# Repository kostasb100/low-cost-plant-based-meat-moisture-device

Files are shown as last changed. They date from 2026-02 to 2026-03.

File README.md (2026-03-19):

# Low-Cost Plant-Based Meat Moisture Content Measurement Device Based on Raspberry Pi 4 B, Its Camera Module 3 NoIR, and a Halogen Lamp

This repository contains work conducted at the Optics and Photonics Laboratory at Niigata University by fourth-year Electronics, Information and Communication Engineering Program student Kostas Martynas Balciunas between 2025 and 2026 for his Bachelor's thesis. The purpose of this repository is to enable students and other individuals to recreate, use and potentially improve the moisture content measurement device that was developed during this period.

## The repository includes:
- Mechanical diagrams of the developed device  
- Software and programs used for the device and its measurement data analysis  
- Electrical circuit diagrams of the developed device  
- Additional materials to assist in recreating the device and the plant-based meat used

## Guide to those seeking to recreate the device:

1) Carefully read the Aim, Basic Theory, Current Results, and Future Work sections of this README.md file to understand the basic concepts of the developed measurement device and it's limitations.
2) Buy the necessary materials to build the measurement device (print the 3D model of the device and assemble the electrical circuits) and prepare the plant-based meat sample (other recipes for plant-based meat samples can also be used).
3) Set up your Raspberry Pi 4 B module (it may be possible to use other Raspberry Pi microcontrollers as well) and install the necessary libraries and software (refer to Programs).
4) Recreate the electrical circuits used in the measurement device (refer to Electrical Circuit Diagrams). Make sure they work as standalone circuits before connecting them to the microcontroller.
5) 3D print and construct the case for the measurement device (refer to Mechanical Diagrams). 3D printing the device is not necessary, since 2D diagrams are provided (Mechanical Diagrams/2D diagrams), and it is possible to recreate the device using cheaper materials such as cardboard or plywood. However, it is important to note that the precision of the measurement device may suffer due to the unevenness of individual components made by hand.
6) Install the electrical circuits and the Raspberry Pi Camera Module 3 NoIR into the case of the device.
7) Prepare the plant-based meat sample for the experiments (refer to Recipe of the plant-based meat used).
8) Conduct experiments and initial image processing using the user manual provided in the User Manual and Guide section of this repository.
9) Conduct comprehensive (batch) post-experiment image processing using Programs/Other Programs/apv_calculator.py.
10) Use other programs to visualize experiment results if necessary.
11) Learn, improve, and enjoy the process. If you notice any issues, make improvements or like to request for the actual data of the individual experiments conducted please contact the creator of this repository (contacts are listed at the bottom of this file).

## Aim
Interest in alternative proteins such as plant-based meats has grown in recent years, but development remains concentrated in regions like North America and Europe due to the need for expensive facilities and equipment. This limits access for developing countries and institutions with restricted budgets, potentially hindering global progress in this field.

Moisture content is a key parameter affecting the texture, taste, and overall quality of plant-based meat products and is typically measured using costly equipment such as spectrometers. This project investigates the feasibility of a low-cost, Raspberry Pi-based imaging device for non-destructive, real-time moisture measurement during product development. It also explores the use of the same device to track changes in moisture content, size, and color over time, providing insight into the sample’s optical and physical properties.

## Basic Theory

Water molecules are known to absorb electromagnetic radiation (light) over a wide range of the electromagnetic spectrum [1]. The relationship between wavelength and the corresponding absorption coeffcient is shown in Figure 1.

<p align="center">
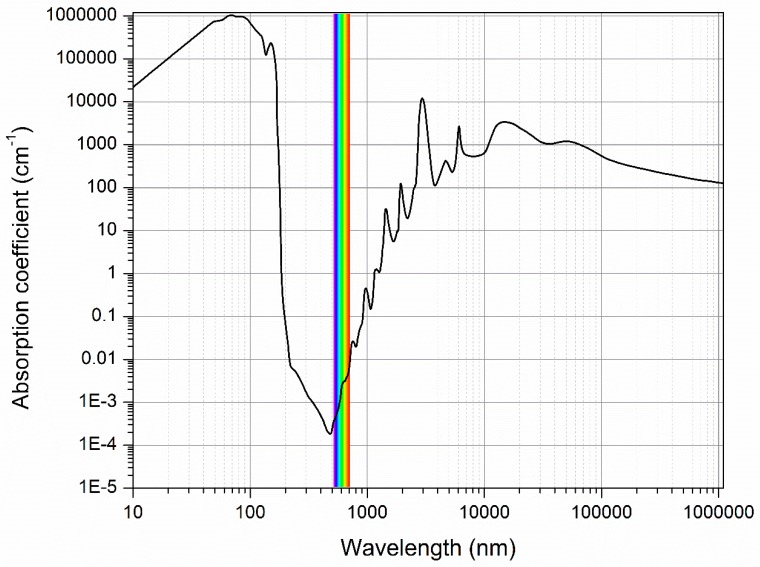
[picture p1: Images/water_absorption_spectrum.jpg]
  
</p>

<p align="center">
  <em>Figure 1. The water absorption spectrum[1].</em>
</p>

In the UV region (100 nm to 400 nm), as well as in the mid-IR (3 µm to 50 µm) and far-IR (50 µm to 1000 µm) regions, water exhibits strong absorption. In the context of food analysis, such strong absorption limits measurements to very thin samples. If light of a particular wavelength entering a sample is absorbed by water to the point that the reflected intensity is very low, it becomes difficult to detect using low-cost equipment. In contrast, water absorption in the near-infrared (NIR;0.7 um to 3 um) region is signi
cantly weaker. As a result, sufficient transmitted intensity can be obtained even for thicker samples, enabling non-destructive analysis of whole plant-based meat products such as hamburger patties with minimal sample preparation. 

<p align="center">
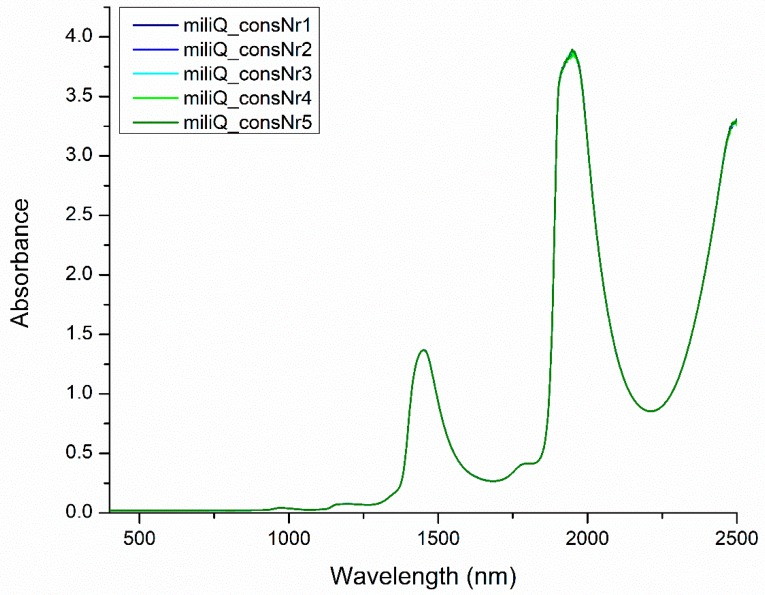
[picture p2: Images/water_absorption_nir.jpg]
  
</p>

<p align="center">
  <em>Figure 2. Near-infrared spectra of pure water[2].</em>
</p>

More than 500 water absorption bands have been identifi
ed in the wavelength range from 400 to 2500 nm [2], but only four main bands, located approximately at 970, 1190, 1450, and 1940 nm, are considered to contain signi
cant information about water structure (moisture)(Figure 2). Among these, the absorption band at approximately 970 nm is of particular importance to this research. Although its absorbance is lower than that of the other main bands, this wavelength
is relevant because some low-cost imaging sensors, such as the Raspberry Pi Camera Module 3 NoIR, are sensitive to wavelengths up to approximately 1000 nm [3]. 

If changes in moisture content affect reflected light intensity, and these changes are captured as variations in average pixel intensities (API) in JPEG images or average pixel values (APV) in RAW (DNG) images, then it may be possible to detect moisture changes using image data alone. 

A low-cost device consisting of a Raspberry Pi 4 B microcontroller, its Raspberry Pi Camera Module 3 NoIR, and other readily available components is proposed for this purpose. If a decrease in moisture content (due to evaporation) consistently corresponds to an increase in pixel intensities or values, this would indicate that the device can be used for moisture analysis.

## Current Results

Figures 3 to 5 show the developed moisture measurement device.The body of the device was fabricated using a 3D printer (Creality K1). It was printed in multiple parts using black 1.75 mm diameter PLA filament (Creality Ender, 3D PLA BLACK 1.75 mm) and assembled using screws or adhesive. The device incorporates a light source consisting of a 4.8 V, 0.5 A halogen lamp (HL) (National, Halogen Miniature Lamp MB-48M5H), which emits both visible and NIR light. A white plastic cap (CP) obtained from a PET bottle and assumed to be made out of either polyethylene or polypropylene was affixed above the lamp to scatter the emitted light. The scattered light is further dispersed using a Fresnel lens (FL) (CAN DO 100 yen shop, Card Magnifier, 2.5 × magnification) placed 4.0 cm from the halogen lamp and subsequently passed through an infrared transmittance filter (IRF) that absorbs wavelengths below 900 nm (FUJIFILM, Infrared Transmittance Filter IR90, 7.5 × 7.5). These optical components were housed inside a small enclosure with an adjustable angle. All experiments were conducted with the enclosure fixed at an angle of 33° relative to the base of the device. The FL was positioned as close as possible to the filter (at a distance of around 1 cm), with the infrared transmittance filter placed at the end of the enclosure facing the sample. The filter was positioned approximately 10 cm from the sample, measured along a line perpendicular from the center of the transmittance filter to the sample surface. The light source was controlled using the circuit described in Electric Circuit Diagrams.

<p align="center">
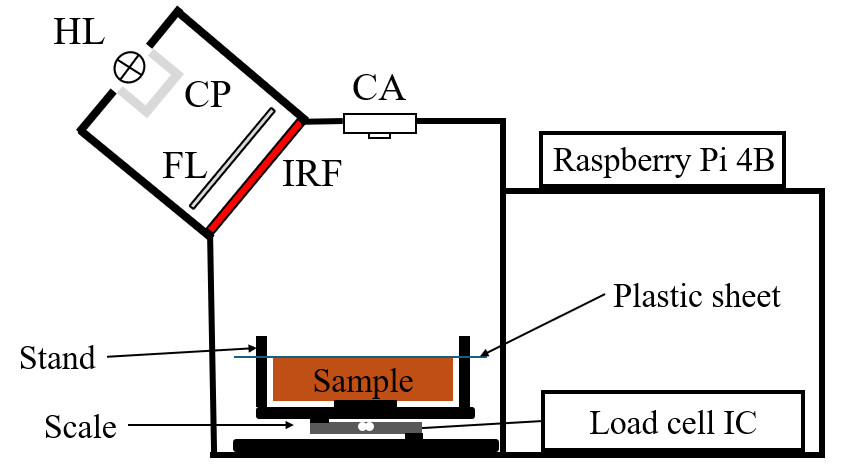
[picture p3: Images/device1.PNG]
  
</p>

<p align="center">
  <em>Figure 3. Simplified image of the developed device.</em>
</p>

<p align="center">
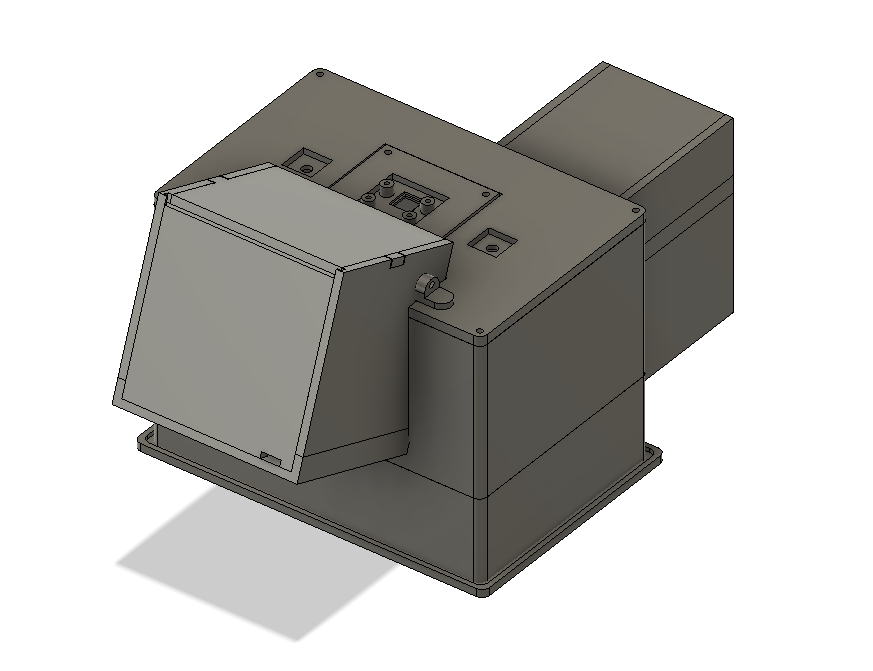
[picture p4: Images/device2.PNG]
  
</p>

<p align="center">
  <em>Figure 4. 3D CAD model of the developed device.</em>
</p>

<p align="center">
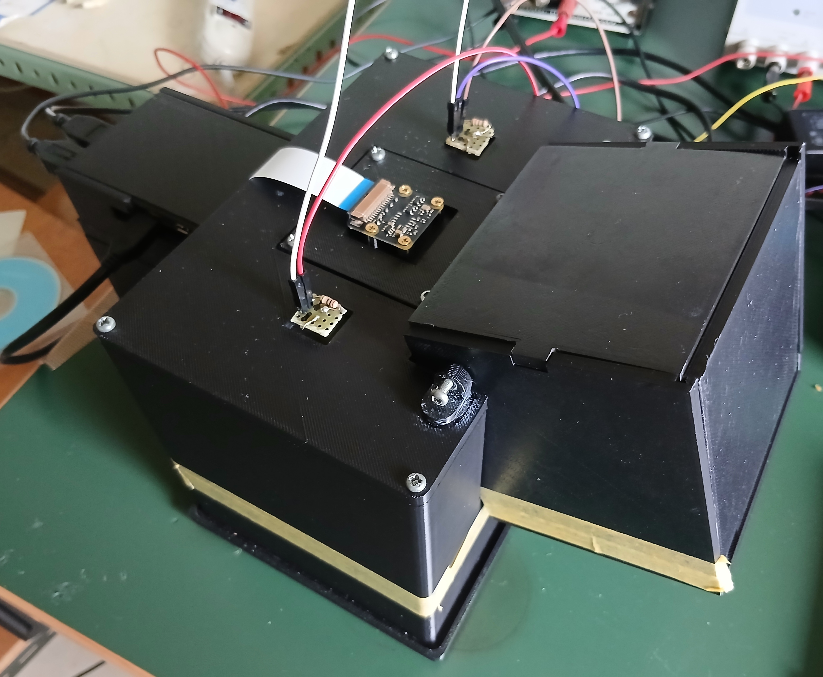
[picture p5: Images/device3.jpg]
  
</p>

<p align="center">
  <em>Figure 5. Assembled device.</em>
</p>

The Raspberry Pi Camera Module~3 NoIR (CA) was positioned directly above the sample location at an approximate distance of 9 cm from the sample surface. CA was mounted using screws and placed in close proximity to the microcontroller, which was also secured using screws. Although not shown in diagram, two white LEDs were installed to the left and right of the camera and were controlled by the microcontroller. These LEDs were used to monitor color changes in the sample. Additional plastic caps were attached to each LED to diffuse their emitted light.

The sample was placed on a scale constructed using a 500 g capacity load cell (Sensorcon, Micro Type Load Cell SC616C) , a 3D-printed black plate and an HX711 chip-based AD converter module (Akitsuki Denshi, AE-HX711-SIP) for signal acquisition. The module and its associated circuitry were housed inside an enclosure attached to the main sample chamber. It is important to note that the scale is only used for the initial experiments and the calibration of the device and is not supposed to be used when the device is fully developed.

An additional platform as shown in Mechanical Diagrams/2D diagrams/SCALE/S6.PNG was later introduced on top of the scale to allow the sample to dry from its bottom surface rather than from its upper surface. This platform was designed in such a way that a piece of translucent plastic cut from a file holder could be placed over the plant-based meat sample and fixed in place.

Many experiments were conducted using the developed moisture measurement device and plant-based meat samples. Two of these experiments are presented here.

### Experiment with the plant-based meat sample without the translucent plastic cover

This experiment was conducted using a plant-based meat sample with its surface uncovered in a dark room under controlled ambient conditions. The temperature was maintained at 24°C, and the experiment took place during dry weather conditions in Niigata, Japan, in January. To minimize the influence of stray light, the device shown in Figure 5 was covered with an additional cardboard enclosure. For the same reason, the monitor used to control the Raspberry Pi microcontroller was oriented away from the device. The mass of the sample was measured using the integrated scale both before and after the experiment, while maintaining identical measurement settings.

The experiment lasted 380 minutes and consisted of 20 cycles acquired at 20-minute intervals. Noise, LED-illuminated, and halogen lamp-illuminated images of the sample were captured in both DNG and JPEG formats, and the corresponding image metadata were stored. The exposure time was set to 150,000 μs, the analogue gain to 1.0, the colour gains to (1.0, 1.0), and the lens position to 10.0. Both AfState and AeState were set to False.

The initial mass of the sample was 34.01 g. Based on the Moisture Content Calculator described in the relevant section, the initial water content of the sample was estimated to be between 18.55 and 19.08 g. The mass of the sample decreased to 32.80 g by the end of the experiment, corresponding to a mass loss of approximately 1.20 g (with an estimated mass loss rate of 0.0032 g/min). Changes in APV over time were evaluated for the region inside the sample, the region outside the sample, and the total image area excluding the shrinkage region. Edge detection was performed using the parameter settings listed in Table 1 with the program described in Programs/Other Programs/apv_calculator.py. These settings were kept constant for all images across all experimental cycles.

<p align="center">
  <em>Table 1. Settings applied to the processed experimental images of a plant-based sample without the plastic cover.</em>
</p>

<div align="center">

| Setting                  | Value   |
|--------------------------|---------|
| Gaussian kernel          | (3, 3)  |
| Sigma x                  | 0       |
| Thresholding value (min) | 44      |
| Thresholding value (max) | 255     |
| Edge kernel              | (3, 3)  |
| Minimum area             | 147762  |
| Maximum area             | 9000000 |

</div>

<p align="center">
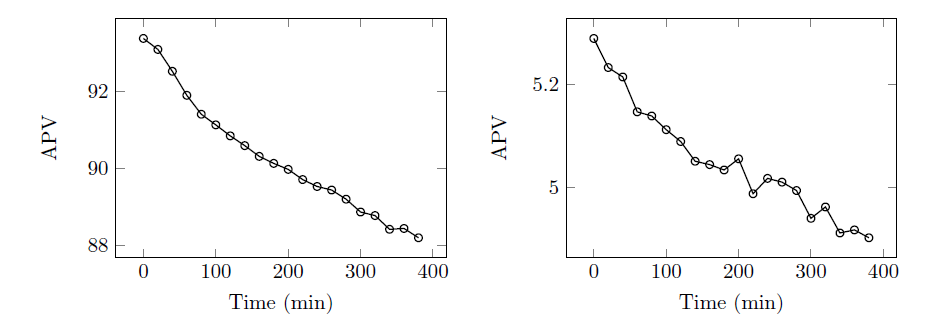
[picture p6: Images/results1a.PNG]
  
</p>

<p align="center">
  <em>Figure 6. APV of the area inside(left) and outside the sample(right)(no plastic cover).</em>
</p>

<p align="center">
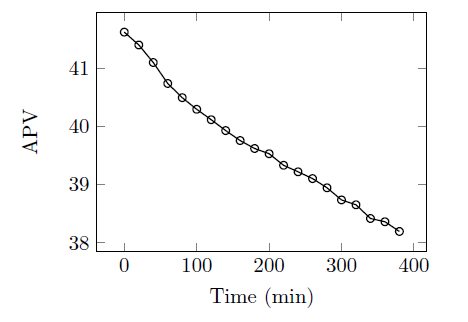
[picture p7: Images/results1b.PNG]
  
</p>

<p align="center">
  <em>Figure 7. APV of the area inside the sample(no plastic cover).</em>
</p>

As shown in Figures 6 and 7, the decrease in sample mass resulted in a decrease in APV across all analyzed image regions, contrary to the previously stated hypothesis. The initial APV of the area inside the sample was 93.38 and decreased by approximately 5.54% to 88.21, at a rate of 0.01361 (a.u.)/min (Figure 6, left). Figure 6 (right) shows that the APV of the area outside the sample decreased from 5.28 to 4.90, corresponding to a reduction of 7.31% at a rate of 0.001 (a.u.)/min, although transient increases in APV were observed at t = 200 min, t = 240 min, and t = 320 min. The APV of the total area, with the shrinkage region excluded, decreased from 41.62 to 38.20, representing a reduction of 8.22%, with an approximate rate of 0.009 (a.u.)/min.

<p align="center">
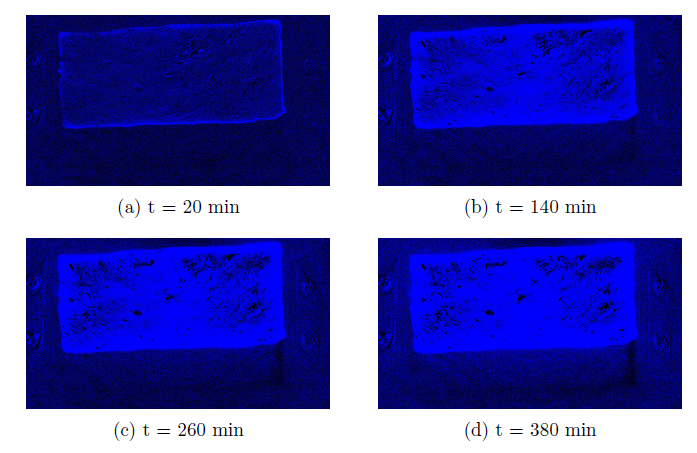
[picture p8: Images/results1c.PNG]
  
</p>

<p align="center">
  <em>Figure 8. Darkened areas of the plant-based sample at different times(no plastic cover).</em>
</p>

<p align="center">
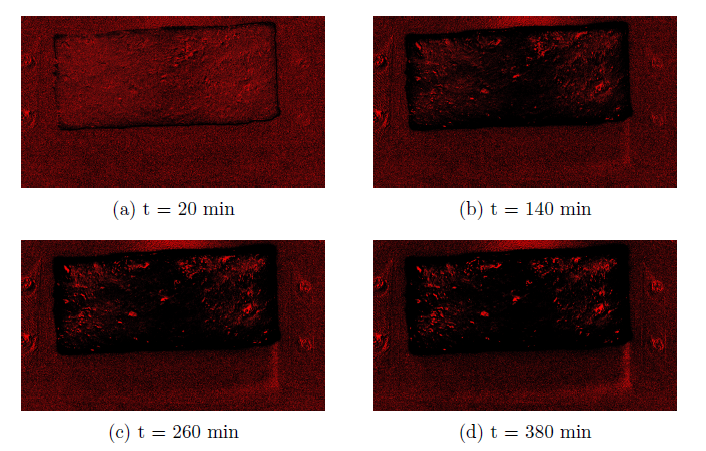
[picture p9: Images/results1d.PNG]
  
</p>

<p align="center">
  <em>Figure 9. Brigthened areas of the plant-based sample at different times(no plastic cover).</em>
</p>

Using Programs/Other Programs/sample_diff_img_generator.py, the spatial distribution of brightness changes in the sample over time was analyzed. The resulting color-mapped images are shown in Figures 8 and 9. Blue regions indicate areas that became darker (decreased in pixel intensities) relative to the initial (reference) image, while red regions indicate areas that became brighter (increased in pixel intensities). The results show that the surface of the sample became significantly darker over time, particularly near the edges and in the central region. Brighter regions were still observed in and around the sample, but their intensity and spatial extent were less prominent throughout the experiment.

Many additional experiments were conducted with the upper surface of the plant-based meat sample uncovered, and all showed similar trends. It is proposed that these results may be due to browning and hardening of the sample surface, as well as stray visible light that the Raspberry Pi Camera Module 3 NoIR can still detect since it is not a specialized NIR camera.

### Experiment with the plant-based meat sample with the translucent plastic cover

To mitigate physical and optical changes in the plant-based meat, a thin translucent plastic sheet was introduced. The sheet was cut from a standard file holder and placed directly on the sample surface without gaps, ensuring full contact. It was secured using screws while applying minimal pressure to avoid deformation or bending of the sample.

The experiment with the translucent plastic sheet in place was conducted under dry weather conditions (December in Niigata, Japan), using the same environmental conditions described previously and a sample with an initial mass of 30.29 g and otherwise nearly identical parameters. The initial water content of the sample was estimated to be between 16.52 and 16.99 g. After 380 minutes, the sample mass decreased to 29.47 g, corresponding to a total mass loss of approximately 0.82 g and an average mass loss rate of approximately 0.0022 g/min. The edge detection parameters used in this experiment are summarized in Table 2.

<p align="center">
  <em>Table 2. Settings applied to the processed experimental images of a plant-based sample(with the plastic cover).</em>
</p>

<div align="center">

| Setting                  | Value   |
|--------------------------|---------|
| Gaussian kernel          | (3, 3)  |
| Sigma x                  | 0       |
| Thresholding value (min) | 45      |
| Thresholding value (max) | 255     |
| Edge kernel              | (3, 3)  |
| Minimum area             | 147762  |
| Maximum area             | 9000000 |

</div>

<p align="center">
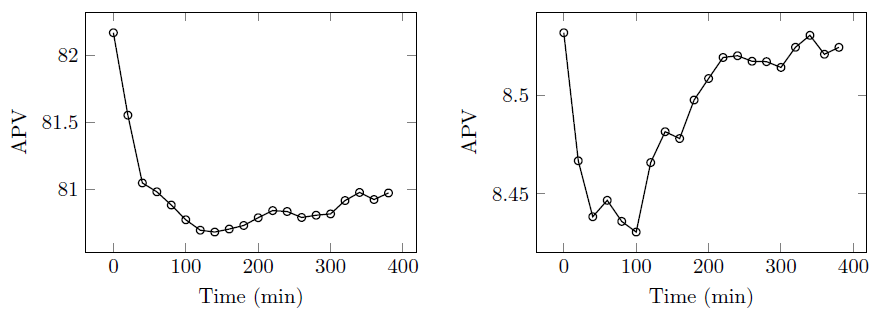
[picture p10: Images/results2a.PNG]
  
</p>

<p align="center">
  <em>Figure 10. APV of the area inside (left) and outside sample(right)(with the plastic cover).</em>
</p>

<p align="center">
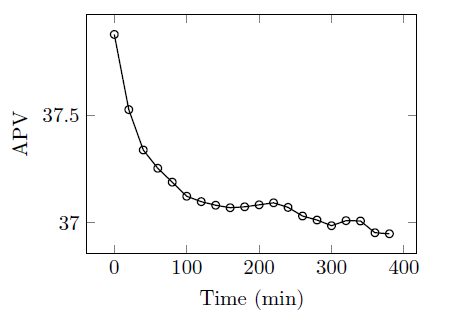
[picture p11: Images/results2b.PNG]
  
</p>

<p align="center">
  <em>Figure 11. APV of the area inside of the sample(with the plastic cover).</em>
</p>

Figure 10 (left) shows that, with the inclusion of the translucent plastic sheet, the APV of the area inside the sample decreased sharply from 82.17 to 80.71 during the first two hours, at a rate of 0.01062 (a.u.)/min. After this initial decrease, the APV gradually increased, reaching 80.97 by the end of the experiment at a rate of 0.00112 (a.u.)/min, corresponding to a net increase of 0.32%. A similar trend was observed for the area outside the sample, where the APV decreased to a minimum value of 8.41 within the first 100 minutes (at a rate of 0.00101 (a.u.)/min) and then increased to 8.52 by the end of the experiment (at a rate of 0.00094 (a.u.)/min), corresponding to a total change of 1.29% (Figure 10, right). In contrast, the APV of the total image area, excluding shrinkage, continued to decrease throughout the experiment, despite minor temporary increases occurring at the same time points as in the other regions (Figure 11). Overall, the total APV decreased from 37.88 to 36.95, representing a reduction of 2.46% at a rate of 0.00244 (a.u.)/min.

<p align="center">
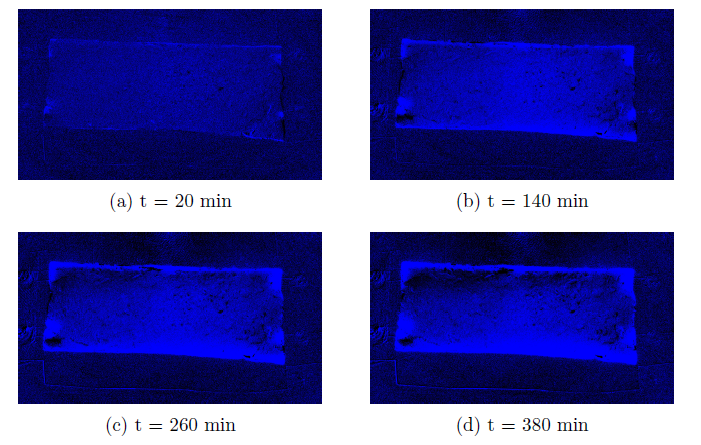
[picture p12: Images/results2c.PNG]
  
</p>

<p align="center">
  <em>Figure 12. Darkened areas of the plant-based sample at different times(with the plastic cover).</em>
</p>

<p align="center">
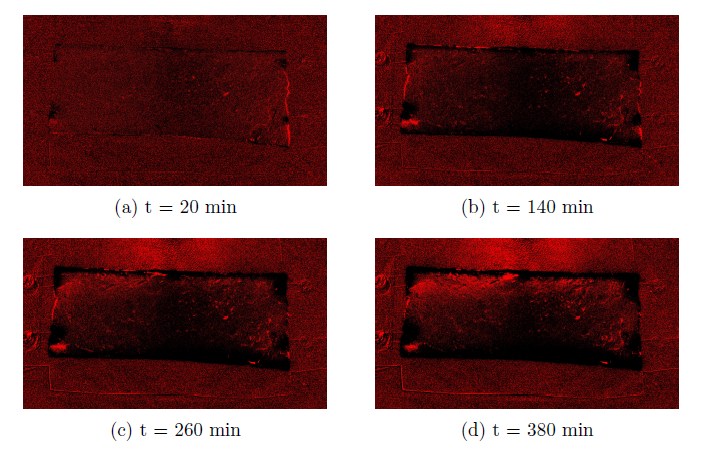
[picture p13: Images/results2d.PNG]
  
</p>

<p align="center">
  <em>Figure 13. Brigthened areas of the plant-based sample at different times(with the plastic cover).</em>
</p>

Figures 12 and 13 show that, when the plastic cover was used, the edges of the plant based sample still exhibited noticeable darkening. However, the central region of the sample, where the plastic cover is assumed to be in direct contact with the surface, did not darken as strongly as in the case without the plastic cover. In addition, the area outside the sample showed a greater tendency toward brightening rather than darkening.

The results above indicate that, with the plastic cover sheet attached, an increase in APV was observed, which is believed to be consistent with the previously described theory and suggests the potential use of the developed device for real-time moisture analysis. However, it is important to note that this increase in APV of the area inside of the plant-based meat sample was small (less than 0.5% from the point at which the increase began) and not linear. This indicates that further improvements and experiments (listed below) are required before the device can be used in any practical applications.

### Attempts to measure the mass of the plant-based during the experiments

Attemps were made to measure the mass of the sample using the HX711 A/C converter based weight scale. However, they proved to bring conflicting results. Figure 14 shows the correlation between the APV change curve of Figure 6(left) and the measurements of the mass.

<p align="center">
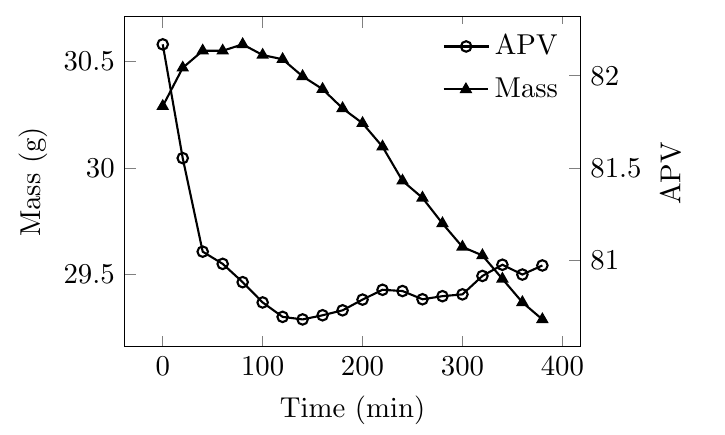
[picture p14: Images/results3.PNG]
  
</p>

<p align="center">
  <em>Figure 14. Temporal evolution of the measured sample mass and the corresponding APV during the experiment with the translucent plastic sheet, illustrating inconsistencies in the mass measurements..</em>
</p>

Reasons for these results and potential improvements are described below.

## Future Work
These are the areas in which the device could potentially be improved:

- Multiple programs used in this research could be combined into a single GUI-based application. This software could be extended to automatically optimize image acquisition and processing parameters, for example by using machine learning techniques.

- Further analysis and experiments are required to determine which regions of the images (inside the sample, outside the sample, or the total image area with shrinkage removed) provide the most valuable information for moisture estimation. It may be necessary to consider all regions to obtain reliable measurements.

- Currently, identical image processing parameters are applied to every experimental cycle, which may introduce errors. It is therefore necessary to evaluate how well the shrinkage area is detected throughout the experiment and potentially implement a time-based shrinkage area detection algorithm that adapts to optical changes in the sample surface due to moisture loss.

- The experimental workflow (capture.py) could be improved by first capturing images at higher shutter speeds (for edge detection) and then at lower speeds only for APV calculations (moisture analysis).

- The correlation between shutter speed (exposure time) and changes in APV/moisture content loss (measured using the HX711-based scale) should be analyzed. There may be an optimal shutter speed at which moisture content changes are most accurately evaluated.

- The weight scale and the algorithm used to acquire measurements should be improved, as the current setup does not provide accurate results. In many experiments, the sample weight increased during the initial hours, which is unlikely under dry winter conditions (December–January in Niigata). This may be due to faulty wiring, measurement drift, or issues in the capture.py pipeline (Programs/Capture Software/capture.py).

- The correlation between changes in APV in different regions of the sample and changes in sample weight should be analyzed (after resolving the scale-related issues).

- The mechanical design of the device could be improved to make it more compact, easier to assemble, and better at preventing stray light from entering the sample chamber.

- The electronics (circuit boards, jumper wires, etc.) could be reorganized to fit more neatly, be shorter, and be easier to remove.

- The distances between the halogen lamp, Fresnel lens, infrared transmittance filter, and the sample were not optimized. Further experiments are required to determine the optimal configuration, as well as the optimal distance between the camera and the sample.

- Different low-cost light sources, such as ~940 nm NIR LEDs, halogen-tungsten lamps, or halogen lamps with different power ratings, could be evaluated to determine their effect on measurement results and to identify the most suitable illumination source.

- Multiple light sources positioned at different angles could also be tested to assess their effect on measurement results, although this would require additional power supplies. Multiple visible light filters could also be used to further reduce the influence of visible and stray light.

- Different plant-based meat recipes can be explored. These may include ingredients such as chickpea flour, soy protein isolate, pea protein isolate, rice protein isolate, tofu, okara (soy pulp remaining after tofu or soy milk production), as well as various root vegetables and legumes. The proposed device could be further developed and calibrated for such variations.

- A more user-friendly manual and repository could be developed to make this project more accessible to people with different backgrounds :P

## References
[1] Muncan, J., Tsenkova, R. Aquaphotomics|From Innovative Knowledge to Integrative Platform
in Science and Technology. Molecules, 24(15), 2742. https://doi.org/10.3390/molecules24152742 , (2019).

[2] Tsenkova, R., Kovacs, Z., Kubota, Y. Aquaphotomics: Near Infrared Spectroscopy and
Water States in Biological Systems. Sub-cellular biochemistry, 71, 189{211, https://doi.org/10.1007/978-3-319-19060-0_8, (2015).

[3] J. Howell, B. Flores, J. Naranjo, A. Mendez, C.C. Vera, C. Koumriqian, J. Jordan, P.
Neethling, C. Groenewald, M. Lovemore, P. Kinsey, T. Krüger. Raspberry Pi multispectral
imaging camera system (PiMICS): a low-cost, skills-based physics educational tool.
10.48550/arXiv.2412.04679, (2024).

## For more additional information, questions or suggestions please contact:

Graduate of Niigata University Kostas Martynas Balciunas (kostbal55@gmail.com)

Professor Samuel Choi, Optics and Photonics Laboratory, Niigata University Samuel Choi (schoi@eng.niigat-u.ac.jp)

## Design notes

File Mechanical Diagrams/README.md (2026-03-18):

Below is an explanation of each component that the measurement device consists of. It is recommended to 3D print the components and assemble them in numerical order.
Some components may not be fully optimized, and their parameters may require further adjustment.

Every component was printed using a Creality K1 3D printer and black PLA filament (Creality Ender, 3D PLA BLACK 1.75mm) and assembled using screws or adhesive.

## Camera stand components of the measurement device (CS1-CS7)
CS1: Component that serves as the main base of the device. The two holes in the middle are used for S2. The small hole at the bottom of the wall is used to pass through the wires of the load cell to the HX711 weight scale module.

CS2 and CS3: Components used to protect the sample inside the measurement device from outside light. CS3 has a hole in the wall so that the lamp stand can be placed at an angle.

CS4 and CS5: Components used as the stand for the Raspberry Pi Camera Module 3 NoIR, which is inserted using component CS6. The two holes at the sides of the camera opening are used for LEDs. These holes can be covered using two CS5 components.

CS6: Component onto which the camera can be screwed.

CS7: Component that can be glued to the surface of CS4 and is used to stabilize the camera stand with screws (two of these components are needed).

## Lamp stand components of the measurement device (L1-L10)

L1: The base component onto which the lamp stand is built. It has multiple evenly spaced cavities into which infrared transmittance filter frames, Fresnel lens frames, and the light source circuit can be inserted.

L2 and L3: Components used as walls for L1. The holes are used for CS7.

L4: Component that serves as the back wall of the lamp stand and can be slid in and out. The small hole at the bottom is used to pass through wires used to drive the lamp source (positive and negative of the 4.8 V power supply, and a wire for the GPIO pin that turns the logic MOSFET on).

L5: Cover lid component of the lamp stand, which can be easily placed and removed.

L6 and L9: Components used to make the Fresnel lens frame. “Frame” here refers to a component made by attaching L6 to L9 (or L7 to L10) in such a way that an optical component, such as a disk, can be inserted into it. This frame is then inserted into L1 at the distance desired by the user.

L7 and L10: Components used to make the infrared transmittance lens frame. The concept is the same as explained for L6 and L9.

L8: Plate onto which the infrared light source is screwed. The hole in the middle is sized to fit a plastic cap from a plastic PET bottle.

## Base components of the measurement device (B1-B4)
B1: Component into which the HX711 module breadboard circuit was placed. The hole on the right side of the wall was used to pass through wires used to power the module, the halogen lamp, and the LEDs through the Raspberry Pi 4B pins. Fours holes at the back are used to connect B1 to a hinge, allowing B2, B3, and B4, along with some of the camera stand components, to be moved in a rotational direction.

B2: Component used to connect B1 to a hinge and to B3 and B4.

B3: Component used to hold the Raspberry Pi 4 B microcontroller. The holes at the bottom of the plate are used to pass through wires to B1 and to pass the ribbon cable of the Raspberry Pi Camera Module 3 NoIR. The hole on the right side is used to pass through the power supply and monitor cables to the Raspberry Pi 4 B microcontroller.

B4: Component used as a lid for B3.

## Scale components of the measurement device (S1-S6)
S1 and S2: S1 is the upper plate of the scale. It is meant to be screwed onto the load cell, the other end of which should be screwed into S2 and connected to the camera stand (CS) plate CS1.

S3: A component that is connected to the screw holes at both ends of S1 (one component for the left side and one for the right side). It is used to hold the plastic cover sheet placed on top of the plant-based meat sample.

S4 and S5: Components that are to be inserted into S3 with the goal of adjusting the height of the plastic cover sheet.

S6: A component that is connected to S1 and used as a stand onto which the plant-based sample should be placed in order to dry mostly through the bottom surface.

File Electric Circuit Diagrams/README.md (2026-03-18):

# Description of the Developed Moisture Measurement Device Circuit

## The circuit consists of the following main parts:
1) Raspberry Pi 4 Model B microcontroller
2) Halogen lamp drive circuit
3) LED illumination circuits (2 circuits)
4) Weight scale circuit that consists of a load cell and a HX711-based A/D converter module

## Below are the detailed explanations of these parts:

1) The microcontroller is powered by a 5 V / 3 A DC power supply. It can also be powered by a power bank (mobile battery) with the same specifications.

2) One pin of the 4.8 V / 2.4 A halogen lamp LA1 (National, Halogen Miniature Lamp MB-48M5H, https://www.monotaro.com/p/5776/7265/) is connected to a DC power supply set to 4.8 V. The other pin is connected to the drain pin of an N-channel MOSFET Q1 (IRLB8721PbF, International Rectifier, https://akizukidenshi.com/catalog/g/g106024/), which acts as a voltage switch powered by a HIGH (3.3 V) signal delivered from GPIO4. R1 (100 ohm) is a gate resistor that controls the switching speed of the MOSFET. R2 (10 k ohm) is a gate-source resistor used to ensure that the MOSFET remains turned off (gate-source voltage set to 0 V) when no signal is applied to the gate pin. When no voltage is applied to the gate pin, the MOSFET behaves as an open circuit. When a 3.3 V signal is applied, it allows drain current to flow from drain to source (ground), thereby turning on the halogen lamp.

3) Two white LEDs are each connected in series with 220 ohm resistors (R3, R4) to limit the current flow. They are connected to pins GPIO07 and GPIO08 so that the LEDs can be controlled by the microcontroller.

4) A 500 g micro type load cell U2 (SC616C, Sensorcon, https://akizukidenshi.com/catalog/g/g112532/) is connected to an A/D converter U1 (AE-HX711-SIP, https://akizukidenshi.com/catalog/g/g112370/), which is based on an HX711 chip. The VDD pin of the AD converter is connected to a 5 V power supply. Its DAT pin is connected to a voltage divider circuit consisting of R5 (20 k ohms) and R6 (10 k ohms) so that only a 3.33 V signal is delivered to the GPIO17 pin (without this, the signal would reach 5 V and potentially damage the microcontroller). The CLK pin is connected to GPIO27. The analog signal (changes in resistance of the load cell) is delivered from the load cell to the AD converter, which converts this signal into a digital signal. The digital signal is then processed by the microcontroller, which outputs a weight measurement.

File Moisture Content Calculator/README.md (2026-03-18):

# Moisture Content Calculator

An excel spreadsheet with which the user can calculate the assumed(theoretical) moisture content of the total mass of the plant-based meat product made from wheat gluten,
miso paste, garlic, nutritional yeast, water as well as negligible spices (paprika powder and black pepper) and its sample of a specific weight. These numbers can then be used
for the potential calibration of the measurement device.

Note that the reference papers used to get the moisture content ratios may not be accurate since products bought in different locations were used to produce the sample.

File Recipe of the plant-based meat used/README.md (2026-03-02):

# Plant-based meat recipe that was used to make the samples for the experiments

## Ingredients used

- Wheat gluten flour (nichie Wheat Gluten Flour, [https://www.amazon.co.jp/dp/B07FSFBTZH?ref=ppx_yo2ov_dt_b_fed_asin_title])
- Miso paste (Hikari Miso, Craft Miso, Nama-Koji, [bought at a local supermarket])
- Nutritional yeast (Arisan Nutritional Yeast, [https://www.amazon.co.jp/-/en/%E3%82%A2%E3%83%AA%E3%82%B5%E3%83%B3-Arisan-Nutritional-Yeast-200g/dp/B00P1XJ4RG?th=1])
- Garlic [bought at a local supermarket]
- Negligible amounts of black pepper and paprika powder
- Tap water

## Ratio of ingredients used to prepare the plant-based meat loaves

| Ingredient           | Total ratio [%] | Water content [%]         |
|----------------------|------------------|----------------------------|
| Wheat gluten flour  | ~43.0            | 4.80–7.40 [1]                 |
| Miso paste           | ~5.00            | 38.50–44.90 [2]               |
| Garlic               | ~0.70            | 64.37–80.07 [3]               |
| Nutritional yeast    | ~1.60            | 8.00 [4]                       |
| Water                | ~49.7            | 100.0                      |
| Black pepper         | < 0.1            | Negligible                 |
| Paprika powder       | < 0.1            | Negligible                 |

For example, in this research two cilinder-shaped loaves were produced using 350 g of gluten, 40 g of miso paste, 6 g of garlic, 13 g of nutritional yeast, and 413 g (ml) of water. Each loaf weighed approximately 400 g and yielded 4 to 6 samples of around 30 g each, with dimensions of 8 cm (length) x 3 cm (width) x 1 cm (thickness). The samples were rectangular in shape and did not have rounded edges.

The sample was prepared in a regular kitchen using the following procedure:

1) The dry ingredients (wheat gluten , nutritional yeast, and negligible amounts of black pepper and paprika powder) were mixed thoroughly in a large bowl.

<p align="center">
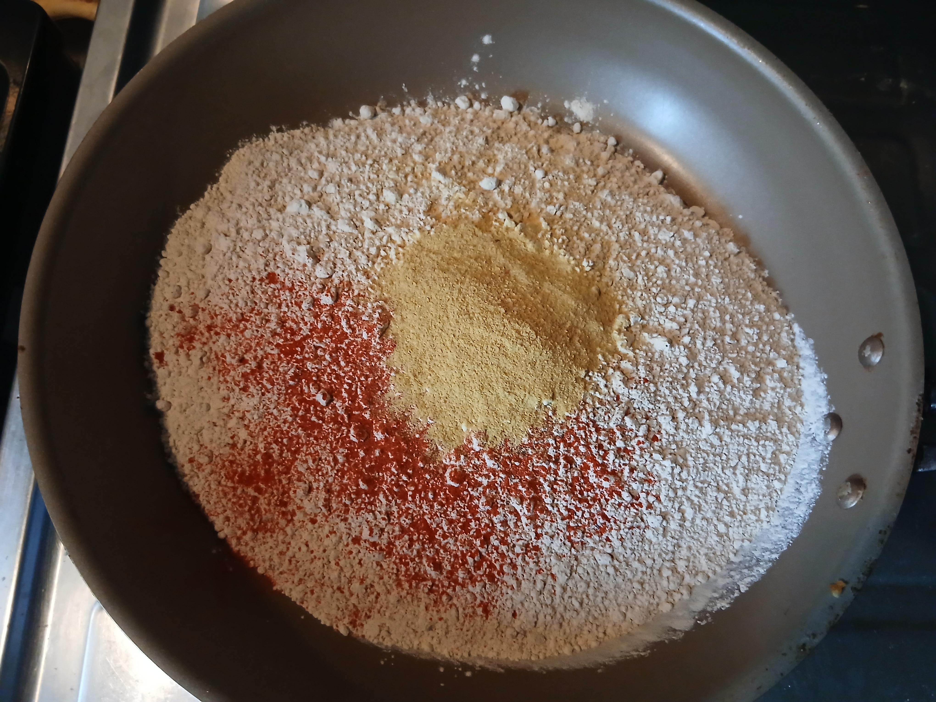
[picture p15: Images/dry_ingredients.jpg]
  
</p>

<p align="center">
  <em>Figure 1. Dry components used in the preparation of the plant-based meat sample.</em>
</p>

2) Minced garlic and miso paste (Hikari Miso, Craft Miso, Nama-Koji) were then added to warm water and stirred until the miso paste was fully dissolved.

3) The wet and dry ingredients were subsequently combined to form a dough.

<p align="center">
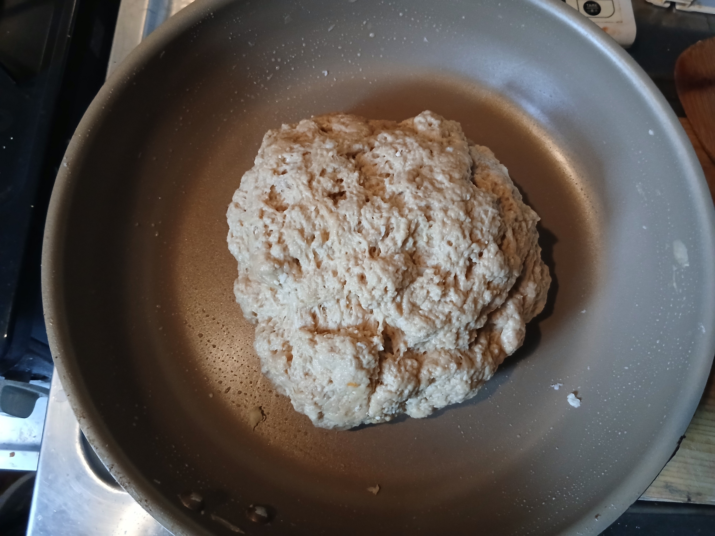
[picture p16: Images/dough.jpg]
  
</p>

<p align="center">
  <em>Figure 2. Dough that was formed by compining the dry and wet ingredients.</em>
</p>

4) The dough was then shaped into loaves and wrapped in aluminum foil lightly coated with olive oil.

<p align="center">
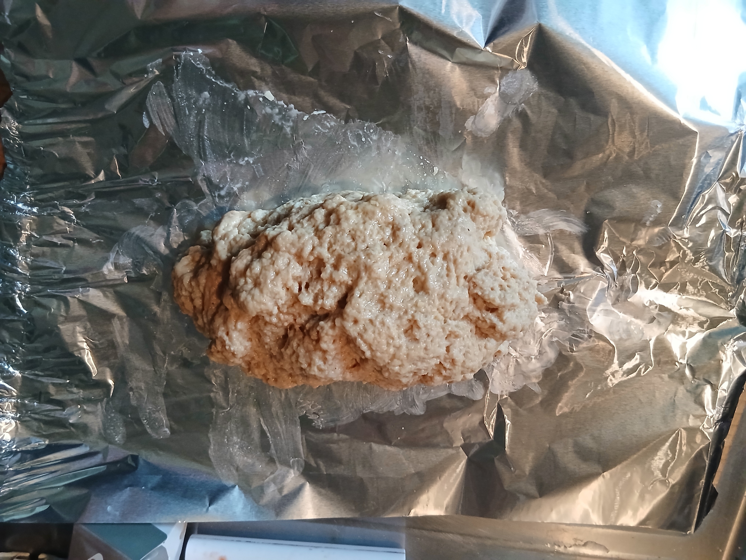
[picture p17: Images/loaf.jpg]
  
</p>

<p align="center">
  <em>Figure 3. Loaf that was lightly coated with olive oil.</em>
</p>

<p align="center">
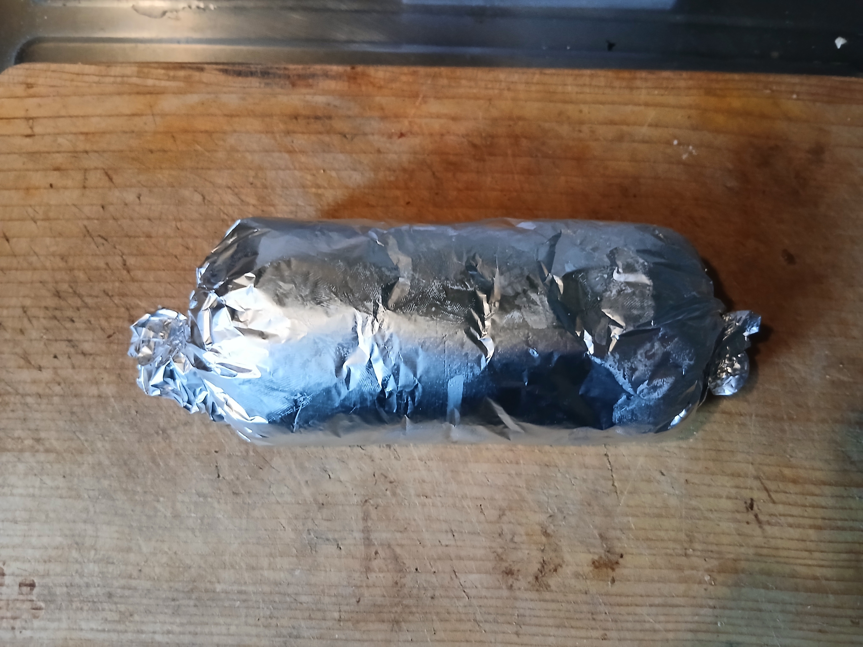
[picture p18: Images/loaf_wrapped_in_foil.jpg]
  
</p>

<p align="center">
  <em>Figure 4. Loaf wrapped in aluminium foil.</em>
</p>

5) The loaves were then steamed for one hour (30 minutes on each side) and allowed to cool for several hours before being either refrigerated or frozen.

<p align="center">
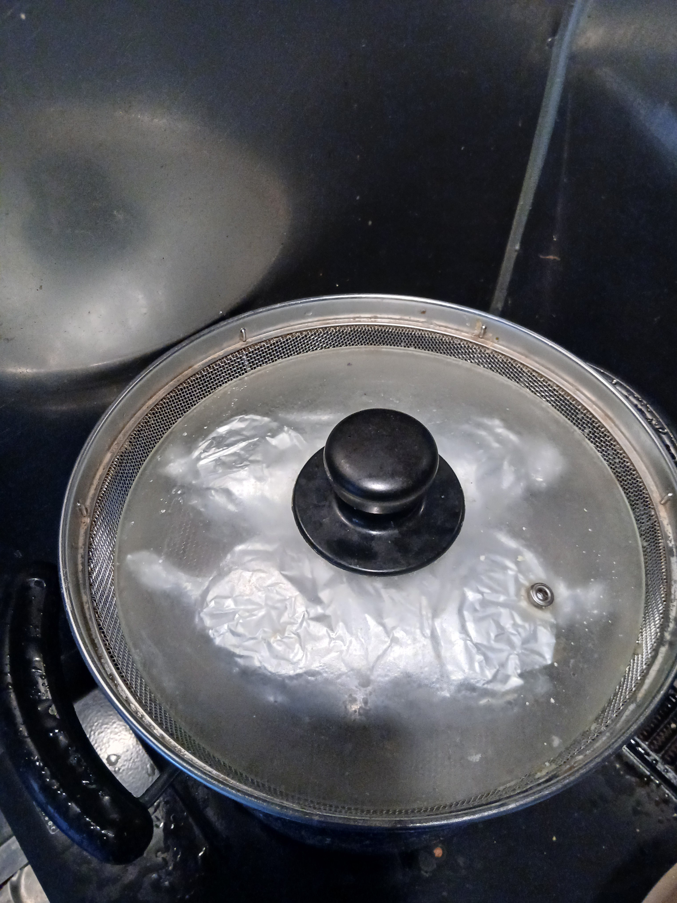
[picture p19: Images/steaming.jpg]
  
</p>

<p align="center">
  <em>Figure 5. Steaming of the plant-based meat.</em>
</p>

6) The cooked loaves were then either frozen or stored in a refrigerator for up to a week.

<p align="center">
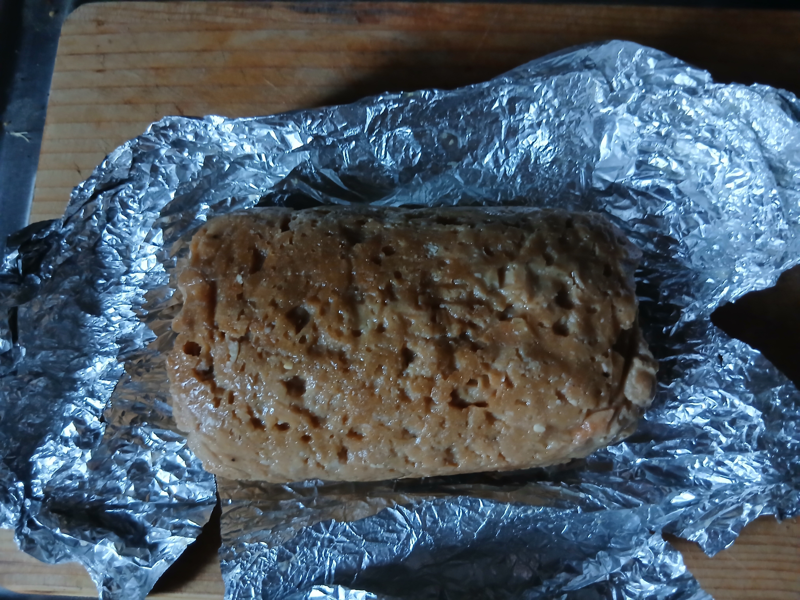
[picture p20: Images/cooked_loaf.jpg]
  
</p>

<p align="center">
  <em>Figure 6. Cooked loaf of the plant-based meat.</em>
</p>

7) On the day of the experiments a 8 cm(lenght) x 3 cm(width) x 1 cm(thickness) rectangle-shaped sample that weighed between 30 and 35 g was cut from inside of the cooked loaf using a regular kitchen knife and stored inside of a sealed plastic bag until the start of the experiments.

<p align="center">
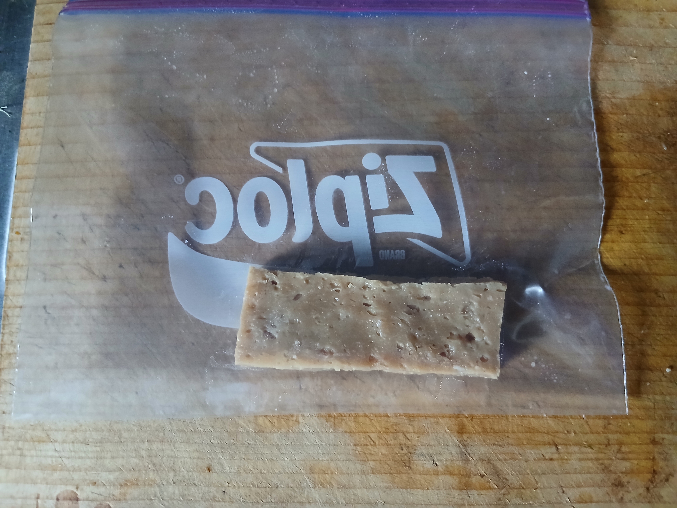
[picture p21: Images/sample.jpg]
  
</p>

<p align="center">
  <em>Figure 7. Plant-based meat sample used in the experiments.</em>
</p>

## References
[1] Schopf, M., Wehrli, M.C., Becker, T. et al. Fundamental characterization of wheat gluten. Eur Food Res Technol 247, 985–997, https://doi.org/10.1007/s00217-020-03680-z, (2021).

[2] Okouchi, R., Sakanoi, Y., Tsuduki, T. Miso (Fermented Soybean Paste) Suppresses Visceral Fat Accumulation in Mice, Especially in Combination with Exercise. Nutrients, 11(3), 560, https://doi.org/10.3390/nu11030560, (2019).

[3] Sunanta, P., Pankasemsuk, T., Jantanasakulwong, K., Chaiyaso, T., Leksawasdi, N., Phimolsiripol, Y., Rachtanapun, P., Seesuriyachan, P., Sommano, S. R. Does Curing Moisture Content Affect Black Garlic Physiochemical Quality? Horticulturae, 7(12), 535,  https://doi.org/10.3390/horticulturae7120535, (2021).

[4] Jach, M. E., Serefko, A., Ziaja, M., Kieliszek, M. Yeast Protein as an Easily Accessible Food Source. Metabolites, 12(1), 63, https://doi.org/10.3390/metabo12010063, (2022).

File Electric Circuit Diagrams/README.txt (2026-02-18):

Description of the Developed Moisture Measurement Device Circuit

The circuit consists of the following main parts:
1) Raspberry Pi 4 Model B microcontroller
2) Halogen lamp drive circuit
3) LED illumination circuits (2 circuits)
4) Load cell and its AD converter circuit

Below are the detailed explanations of these parts:

1) The microcontroller is powered by a 5 V / 3 A DC power supply. It can also be powered by a power bank (mobile battery) with the same specifications.

2) One pin of the  4.8V/2.4A halogen lamp (National, Halogen Miniature Lamp MB-48M5H, https://www.monotaro.com/p/5776/7265/) is connected to a 
DC power supply set to 4.8V.

3) Two white LEDs are connected separately to 220 ohm resistors to reduce current flow and to pins GPIO07 and GPIO08, so that they
can be controlled by a microcontroller.

4) A 500 g micro type load cell U2 (SC616C, Sensorcon, https://akizukidenshi.com/catalog/g/g112532/) is connected to an AD converter U1
(AE-HX711-SIP, https://akizukidenshi.com/catalog/g/g112370/) which is based on a HX711 chip.

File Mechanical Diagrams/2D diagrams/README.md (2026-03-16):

This directory contains mechanical drawings of each the individual parts of the measurement device.

The parts(components) are split into 4 categories:

1) BASE: 4 components (B1-B4)
2) LAMP STAND: 10 components (LS1-LS10)
3) CAMERA STAND: 7 components (CS1-CS7)
4) SCALE: 6 components (S1-S6)

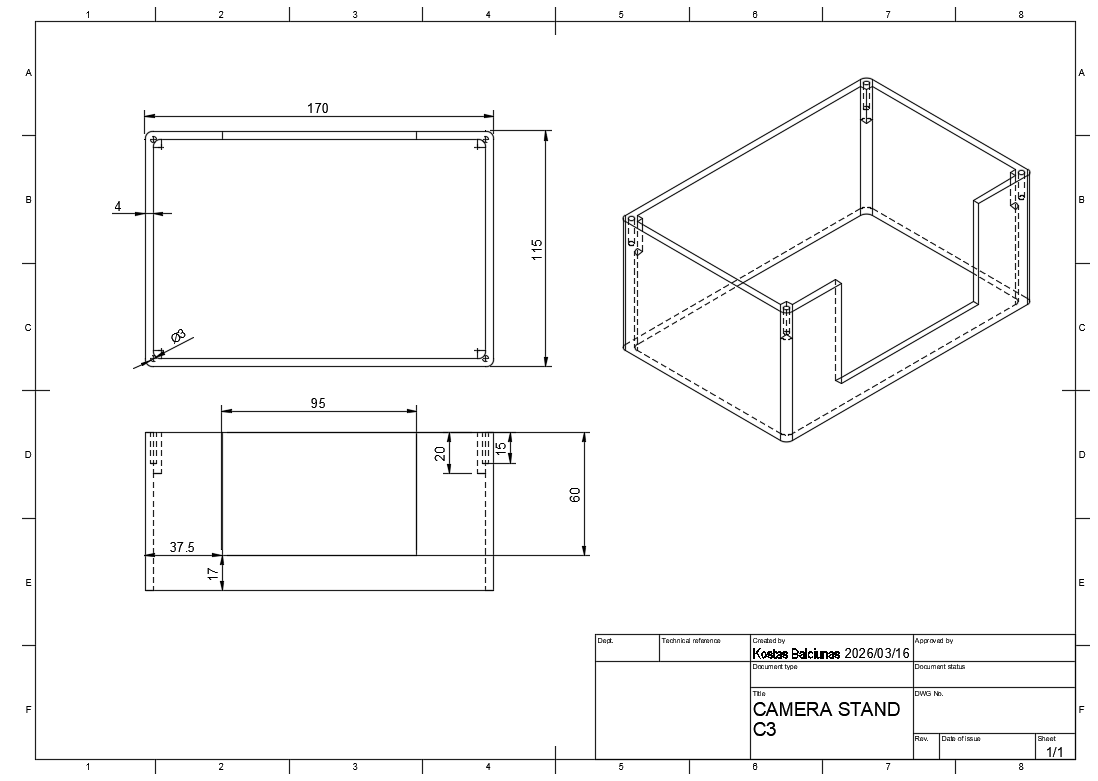
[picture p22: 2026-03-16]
Mechanical Diagrams/2D diagrams/CAMERA STAND/CS3.PNG

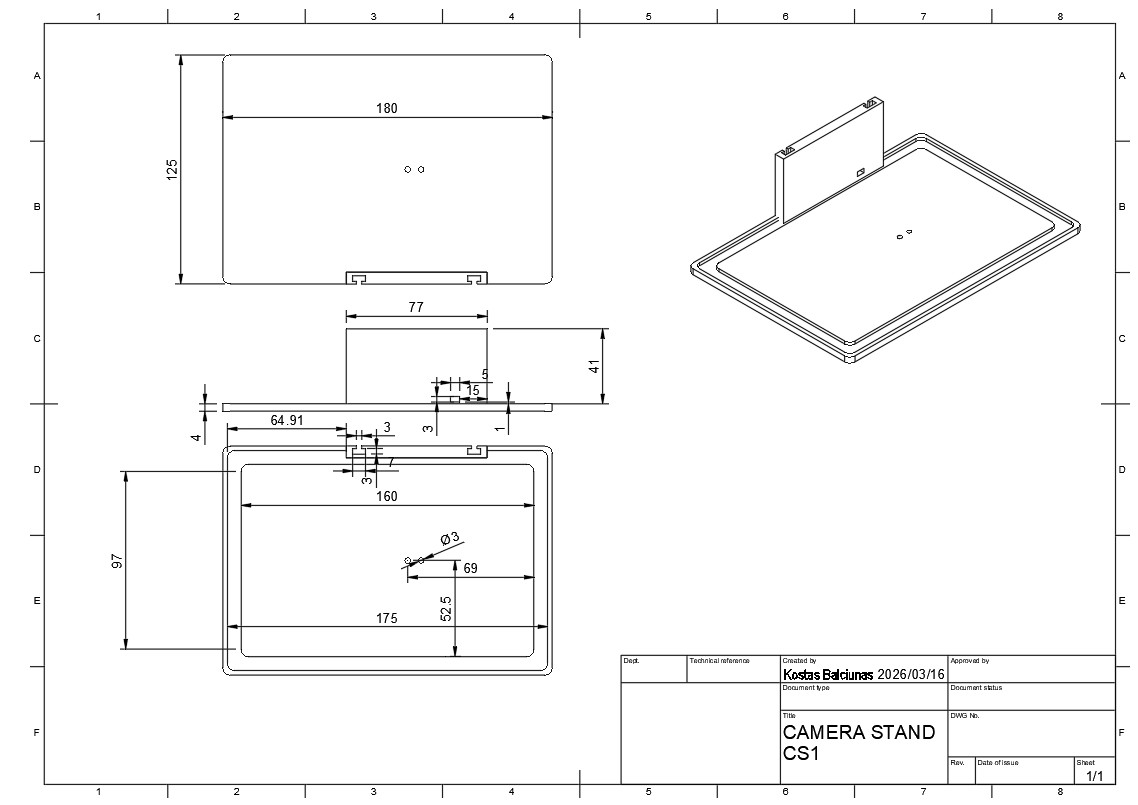
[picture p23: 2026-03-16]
Mechanical Diagrams/2D diagrams/CAMERA STAND/CS1.PNG

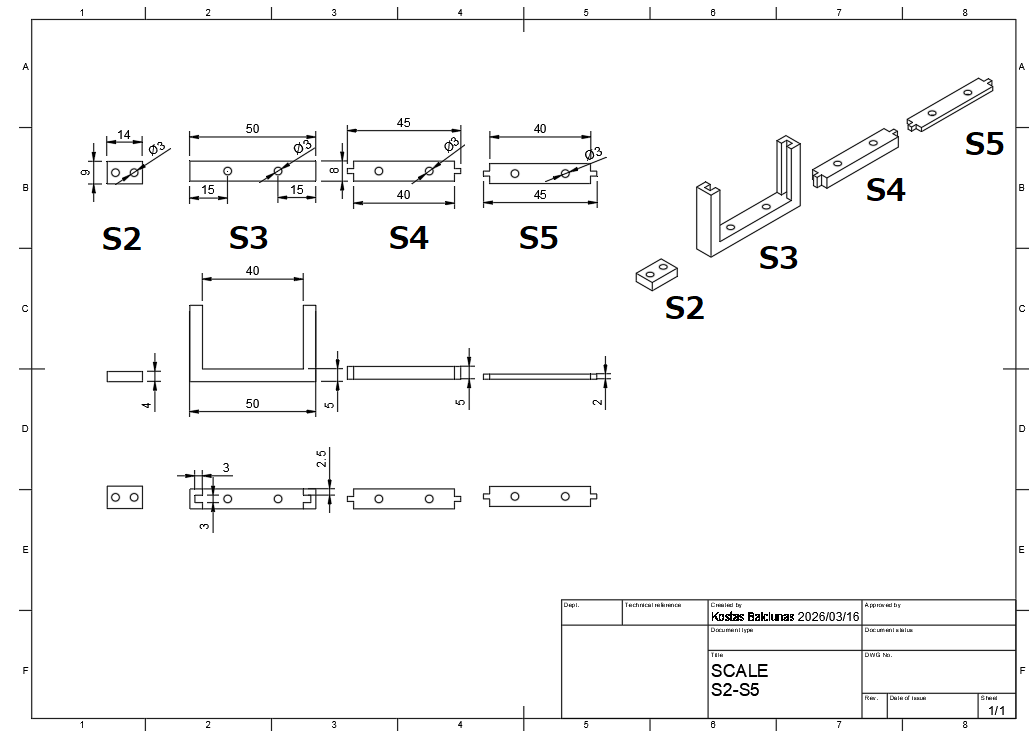
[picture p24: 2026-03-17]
Mechanical Diagrams/2D diagrams/SCALE/S2-S5.PNG

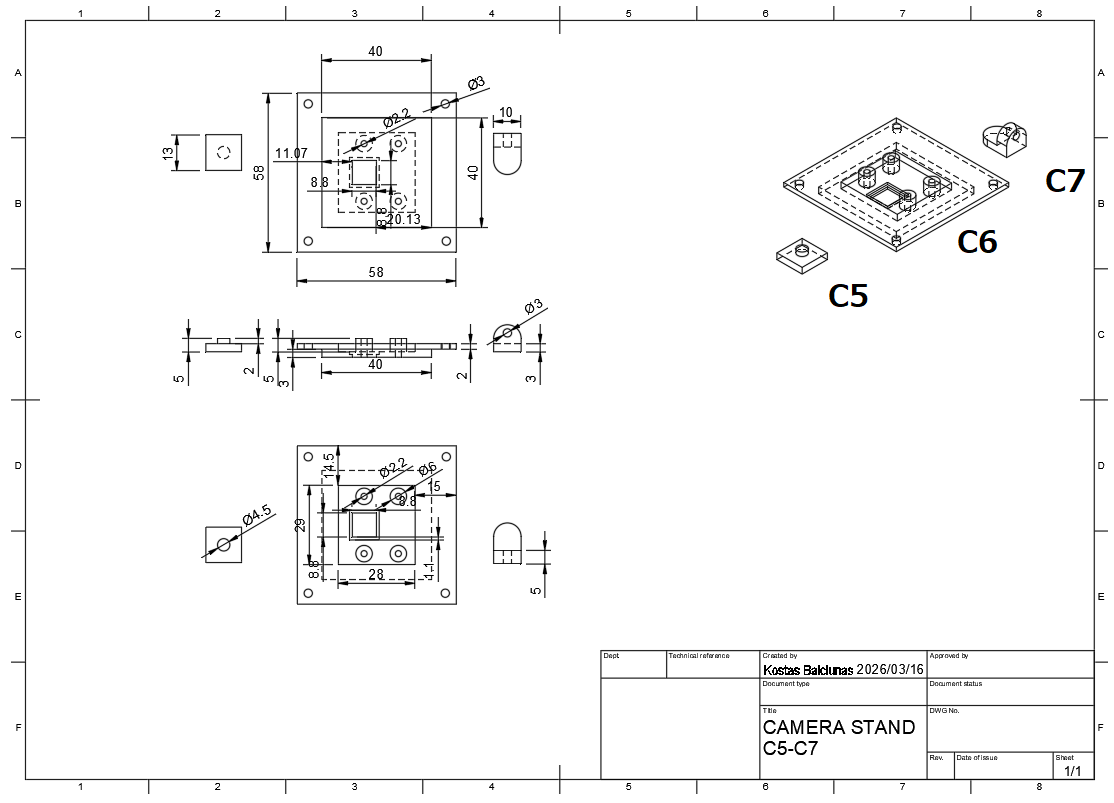
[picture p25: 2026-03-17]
Mechanical Diagrams/2D diagrams/CAMERA STAND/CS5-CS7.PNG

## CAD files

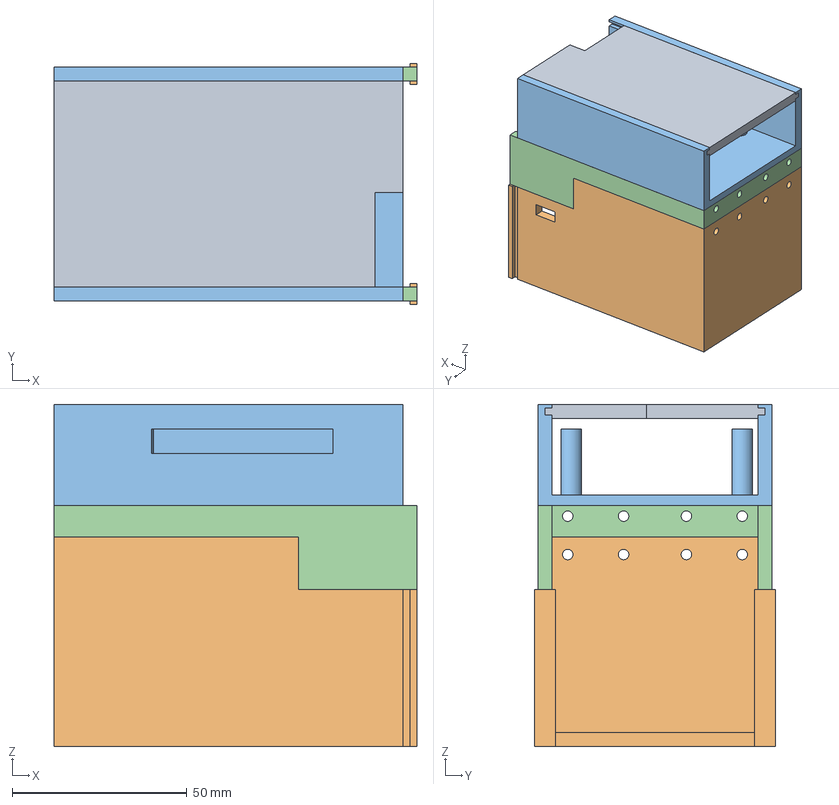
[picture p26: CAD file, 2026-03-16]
Mechanical Diagrams/3D CAD model (STEP)/BASE/BASE.step
104.0 x 69.0 x 98.0 mm
B4
B1
B3
B2

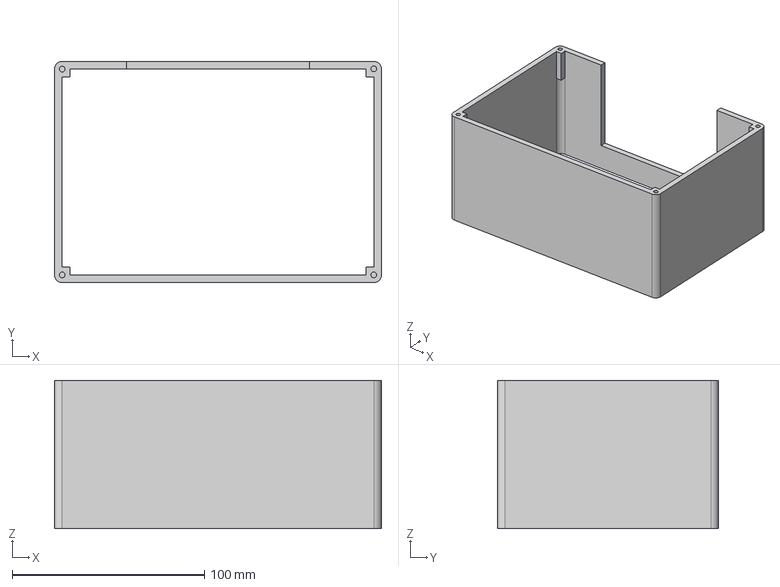
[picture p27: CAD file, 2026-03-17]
Mechanical Diagrams/3D CAD model (STEP)/CAMERA STAND/CS3.step
170.0 x 115.0 x 77.0 mm

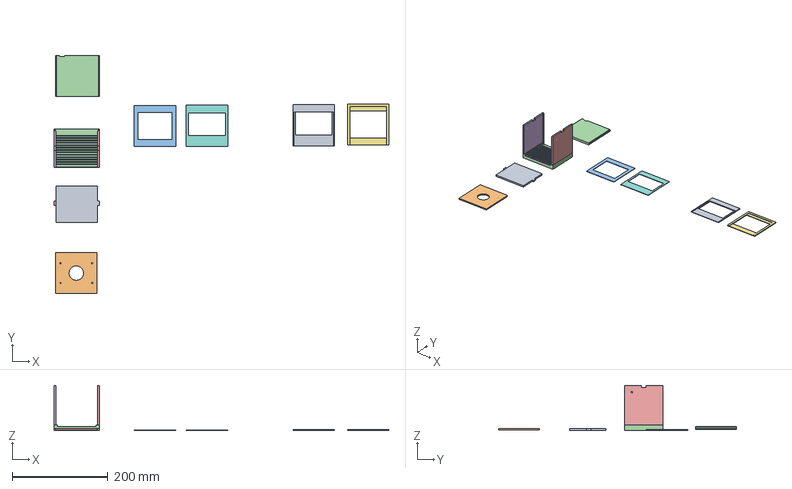
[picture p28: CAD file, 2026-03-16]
Mechanical Diagrams/3D CAD model (STEP)/LAMP STAND/LAMP STAND.step
698.8 x 497.4 x 94.0 mm
L5
L1
L2
L3
L10
L7
L9
L8
L6
L4

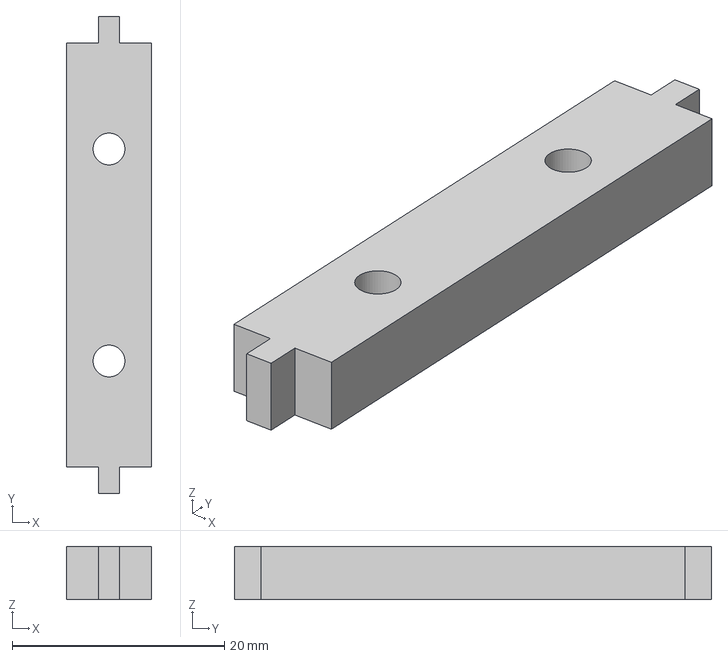
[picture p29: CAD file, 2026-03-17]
Mechanical Diagrams/3D CAD model (STEP)/SCALE/S4.step
8.00 x 45.0 x 5.00 mm

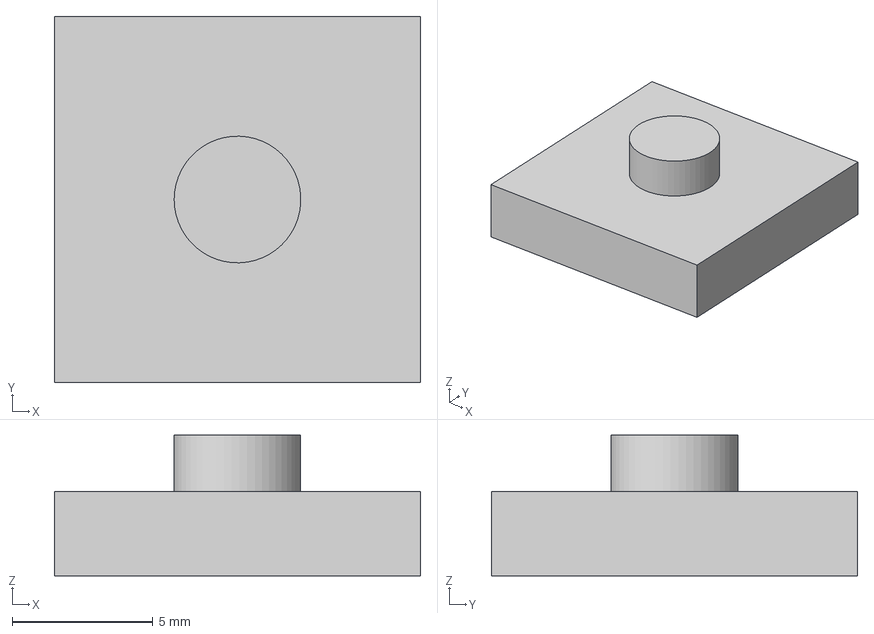
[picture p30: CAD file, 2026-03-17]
Mechanical Diagrams/3D CAD model (STEP)/CAMERA STAND/CS5.step
13.0 x 13.0 x 5.00 mm

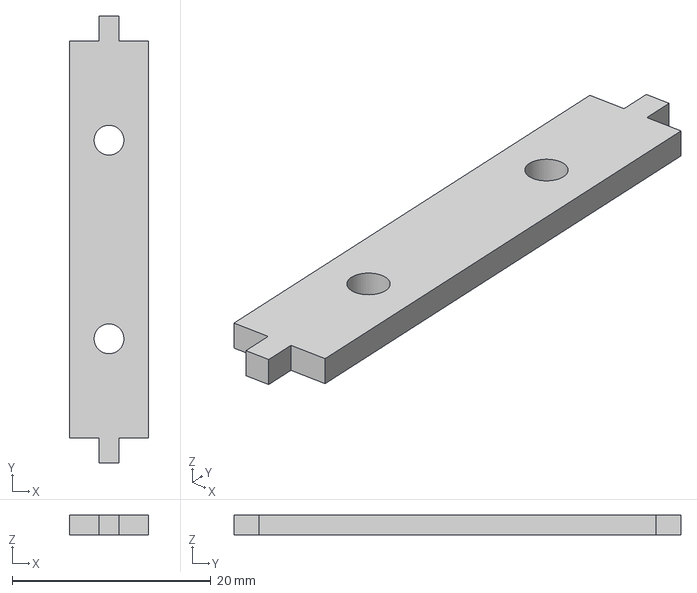
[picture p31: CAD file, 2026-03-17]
Mechanical Diagrams/3D CAD model (STEP)/SCALE/S5.step
8.00 x 45.0 x 2.00 mm

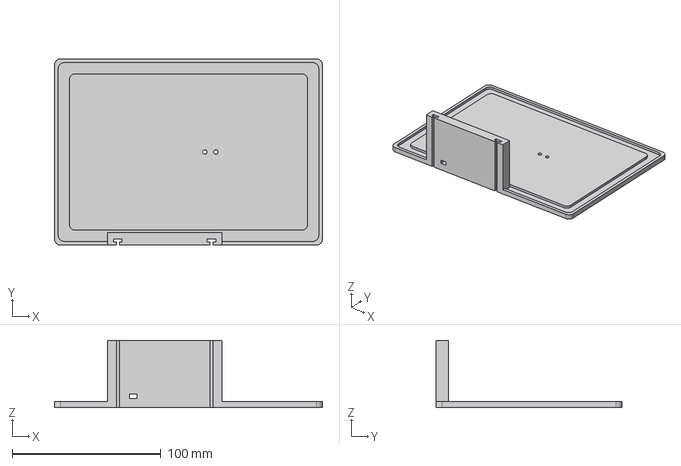
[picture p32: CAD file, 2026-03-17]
Mechanical Diagrams/3D CAD model (STEP)/CAMERA STAND/CS1.step
180.0 x 125.0 x 45.0 mm

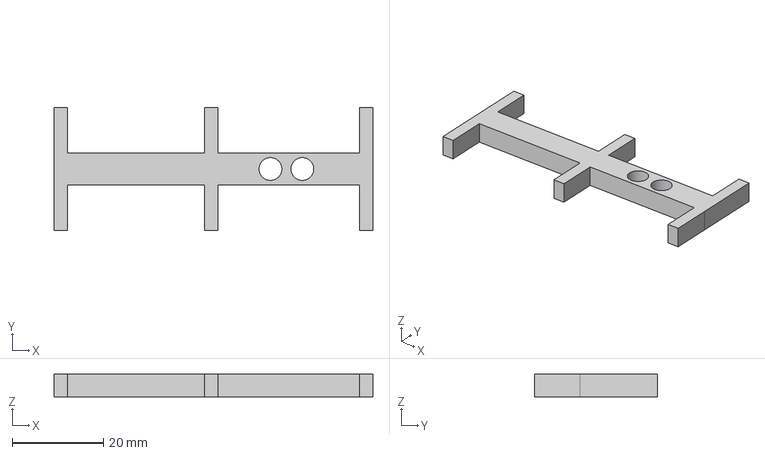
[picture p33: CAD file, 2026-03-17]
Mechanical Diagrams/3D CAD model (STEP)/SCALE/S6.step
70.0 x 27.0 x 5.00 mm

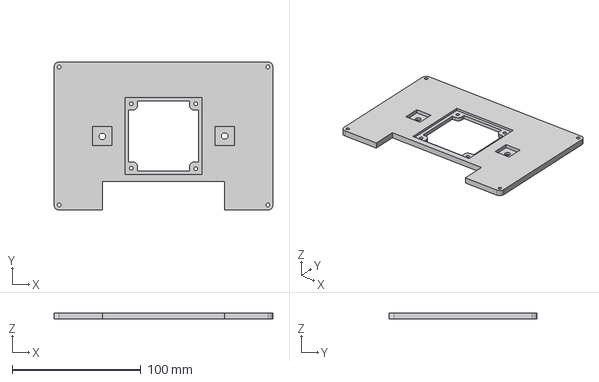
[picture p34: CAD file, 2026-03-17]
Mechanical Diagrams/3D CAD model (STEP)/CAMERA STAND/CS4.step
170.0 x 115.0 x 5.00 mm

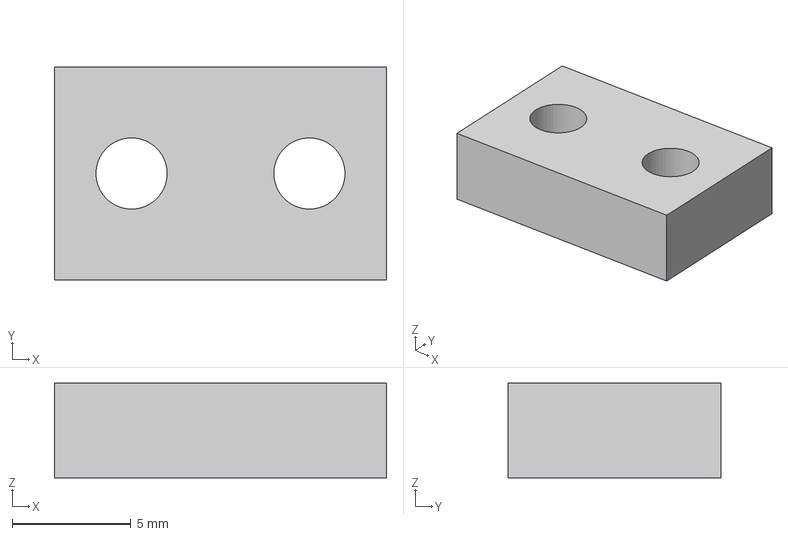
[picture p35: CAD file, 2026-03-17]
Mechanical Diagrams/3D CAD model (STEP)/SCALE/S2.step
14.0 x 9.00 x 4.00 mm

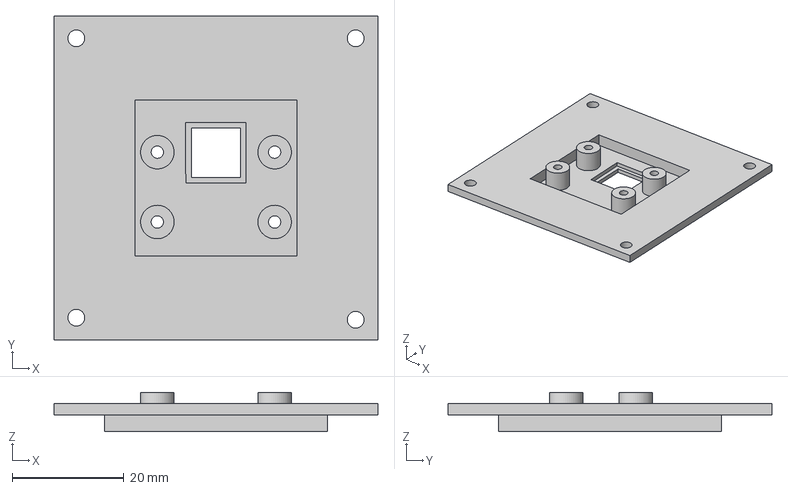
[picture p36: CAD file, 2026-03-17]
Mechanical Diagrams/3D CAD model (STEP)/CAMERA STAND/CS6.step
58.0 x 58.0 x 7.00 mm

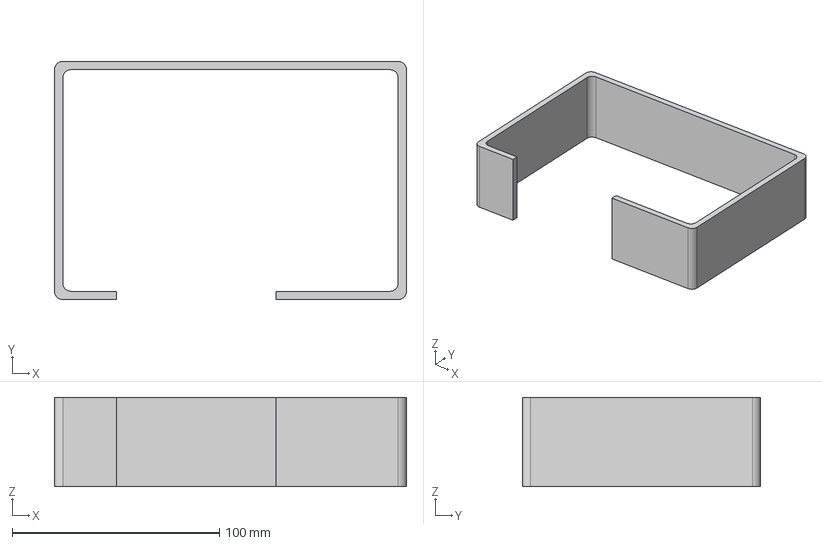
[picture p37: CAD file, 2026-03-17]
Mechanical Diagrams/3D CAD model (STEP)/CAMERA STAND/CS2.step
170.0 x 115.0 x 43.0 mm

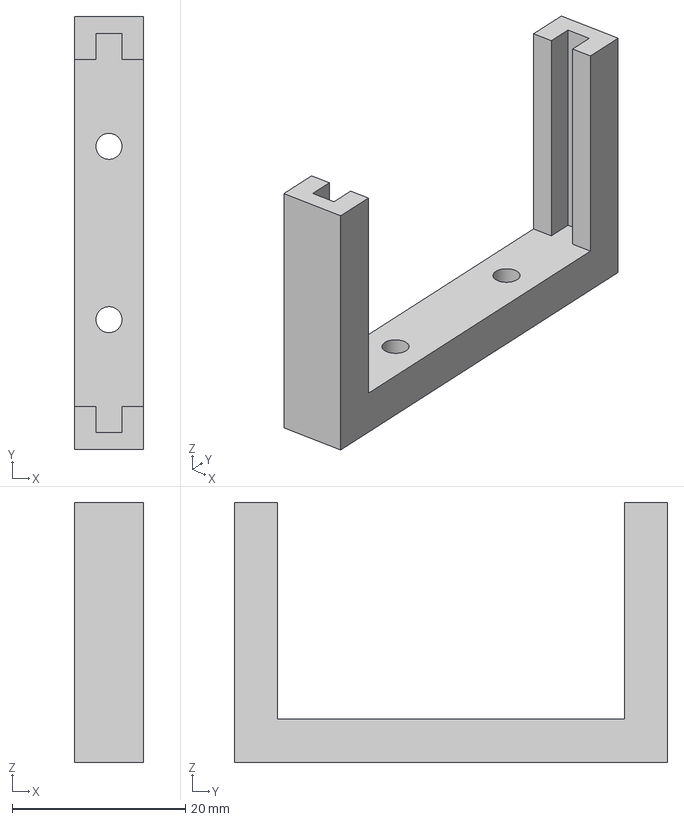
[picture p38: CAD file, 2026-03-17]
Mechanical Diagrams/3D CAD model (STEP)/SCALE/S3.step
8.00 x 50.0 x 30.0 mm

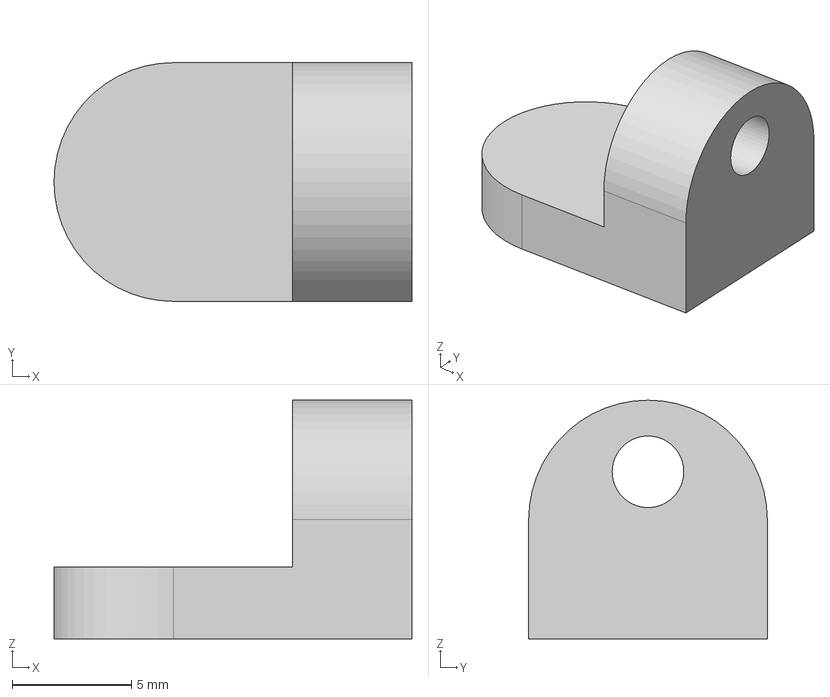
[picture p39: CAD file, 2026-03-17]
Mechanical Diagrams/3D CAD model (STEP)/CAMERA STAND/CS7.step
15.0 x 10.0 x 10.0 mm

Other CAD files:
Mechanical Diagrams/3D CAD model (STEP)/SCALE/S1.step
Mechanical Diagrams/3D CAD model (Autodesk)/BASE/BASE.f3d
Mechanical Diagrams/3D CAD model (Autodesk)/CAMERA STAND/CS1.f3d
Mechanical Diagrams/3D CAD model (Autodesk)/CAMERA STAND/CS2.f3d
Mechanical Diagrams/3D CAD model (Autodesk)/CAMERA STAND/CS3.f3d
Mechanical Diagrams/3D CAD model (Autodesk)/CAMERA STAND/CS4.f3d
Mechanical Diagrams/3D CAD model (Autodesk)/CAMERA STAND/CS5.f3d
Mechanical Diagrams/3D CAD model (Autodesk)/CAMERA STAND/CS6.f3d
Mechanical Diagrams/3D CAD model (Autodesk)/CAMERA STAND/CS7.f3d
Mechanical Diagrams/3D CAD model (Autodesk)/LAMP STAND/LAMP STAND.f3d
Mechanical Diagrams/3D CAD model (Autodesk)/SCALE/S1.f3d
Mechanical Diagrams/3D CAD model (Autodesk)/SCALE/S2.f3d
Mechanical Diagrams/3D CAD model (Autodesk)/SCALE/S3.f3d
Mechanical Diagrams/3D CAD model (Autodesk)/SCALE/S4.f3d
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

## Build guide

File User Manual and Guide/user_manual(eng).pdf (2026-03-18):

## User manual for conducting experiments with the developed measurement device

## 1 Preparation Before the Experiment

1. Prepare the plant-based meat sample that will be put inside of the measurement device.
2. Set the room temperature to be constant using air conditioning (for example to 24 ℃ in winter).
3. Check the output voltage of the DC power supply (HX711 based weight scale module: 5.0 V, light source(0.5 A / 4.8 V halogen lamp): 4.8 V).
4. Check the wiring connections (refer to the circuit diagram on the last page).

## 2 Scale calibration (Optional)

1. Turn on the power of the Raspberry Pi, the scale circuit IC and the light source.
2. Use Geany to launch hx711 scale calibration.py (refer to Programs/Other Programs of the same depository).
3. Place an object with a weight that is known(for example a coin) on the scale and enter it’s weight in the terminal (this number has to be an integer). Record the value of the “Reference Unit” shown in the terminal.
4. Use Geany to open hx711 scale.py (refer to Programs/Other Programs of the same depository) and change the value of the “Reference Unit” to the one acquired in the previous step.
5. Run hx711 scale.py, place the plant-based meat sample on the scale, and record its initial mass before conducting the experiment.

1

## 3 Pre-experiment Setup of Developed Capture Software(capture.py)

### 3.1 Camera Settings

1. Use Geany to launch capture.py (listed in Programs/Capture Software).
2. Enter the camera settings in the first tab.
- Shutter speed: (26.5 µs ∼ 112 s)
- Lens Position (0.0 ∼ 10.0)
- Colour gains [Red, Blue]: (0.0 ∼ 32.0, 0.0 ∼ 32.0)
- Analog Gain: (1.0 ∼ 16.0)
3. Enter the light source settings
- Lamp Drive: Select the pin for the light source (near-infrared light source) (GPIO4 ∼ GPIO27)
- Pre-heat: Enter the pre-heat time (s)

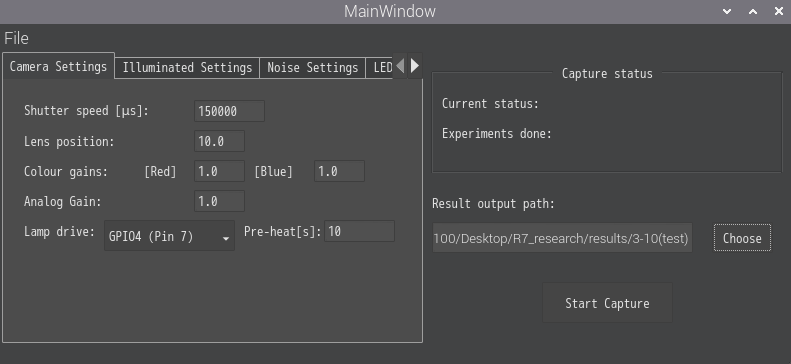
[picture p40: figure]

Figure 1: Camera Settings Tab

2

### 3.2 Illuminated Settings

1. Enter the capture settings for when the light source (near-infrared light source) is turned on.
- Capture NIR illuminated images: Select whether to capture images with the NIR light source turned on (optional).
- Illuminated image count: Number of images to capture while the light source is on.
- Pause between capture: Waiting time between captures (s).
- Save raw images: Select whether to save raw images (DNG format) (optional).
- Illuminated image name: Image name (saved in the format “image name + image number”).

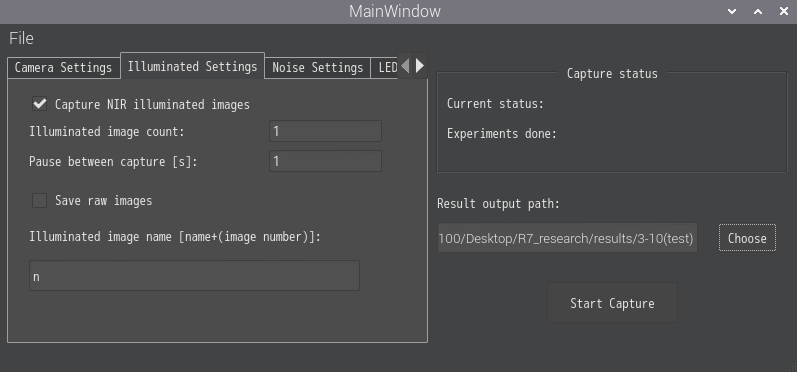
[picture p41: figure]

Figure 2: Illuminated Settings Tab

3

### 3.3 Noise Settings

1. Enter the capture settings when the light source is turned off (noise capture).
- Capture noise images: Select whether to capture images with the NIR light source turned on (optional).
- Noise image count: Number of images to capture.
- Pause between capture: Waiting time between captures (s).
- Save raw image: Select whether to save raw images (DNG format) (optional).
- Noise image name: Image name (saved in the format “image name + image number”).

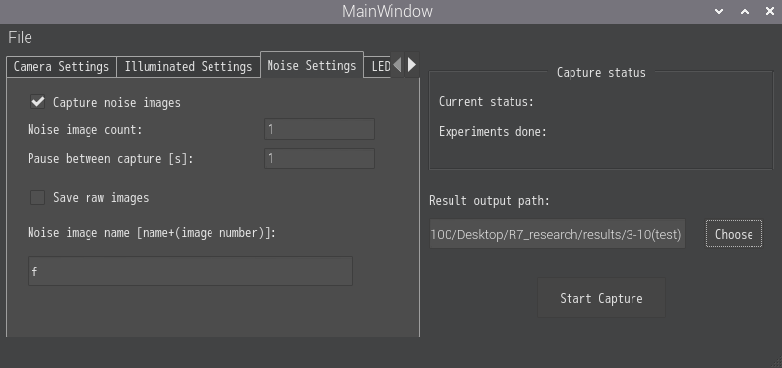
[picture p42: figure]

Figure 3: Noise Settings Tab

4

### 3.4 LED Settings (Optional)

1. Enter the capture settings when the LEDs are turned on.
- LED illuminated capture checkbox: Select whether to capture images when the LEDs are turned on (optional).
- LED1, LED2: Select the pin number for each LED (GPIO4 ∼ GPIO27).
- Illuminated image count: Number of images to capture.
- Pause between capture: Waiting time between captures (s).
- Save raw image: Select whether to save raw images (DNG format) (optional).
- LED illuminated image name: Image name (saved in the format “image name + image number”).

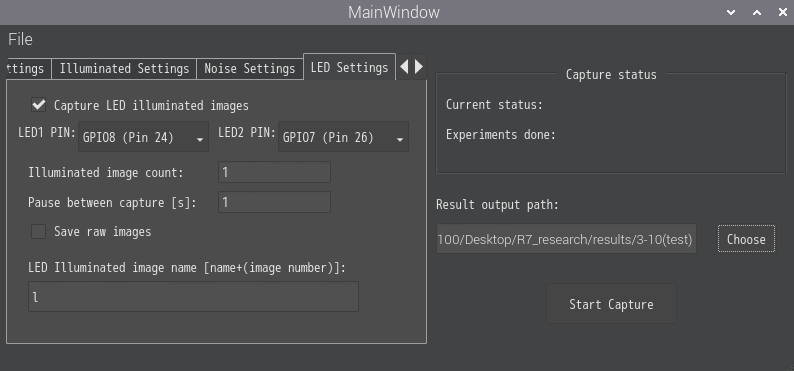
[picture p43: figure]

Figure 4: LED Settings Tab

5

### 3.5 Experiment Settings

1. Enter the advanced settings for experiment capture。
- Get metadata of each capture: Select whether to save metadata for each capture (camera settings, actual values, camera temperature, etc.) (optional).
- Single Shutter Speed / Multiple Shutter Speed: Select whether to perform the experiment with a single or multiple exposure times. If multiple is selected, enter the range in µs (from the exposure time in From to the exposure time in To, varying with the step size specified by By).
- Number of experiments: Specify the number of experiments. One experiment consists of a sequence of operations: mass measurement, noise imaging, LED illuminated imaging, light source pre-heating, and imaging with the light source turned on.
- Time between experiments (TBE): Specify the waiting time between experiments (min). The actual waiting time is “TBE −pre-heat time”.
- Result output path: The destination for saving each image, the metadata of each image, and the mass measurement results.

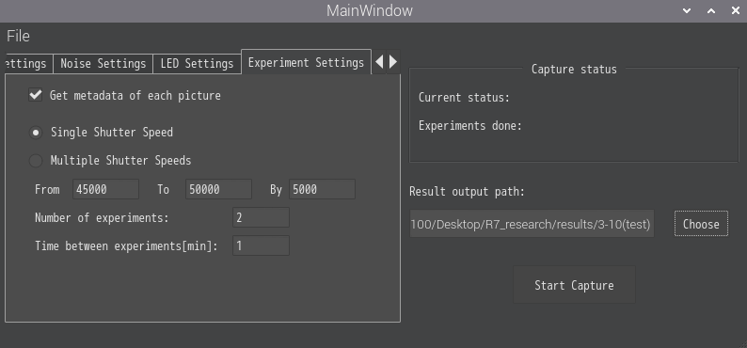
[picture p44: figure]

Figure 5: Experiment Settings Tab

6

### 3.6 Scale Settings (Optional)

1. Enter the scale settings.
- Weigh the sample during experiments: Select whether to measure the mass of the sample during the experiments (optional).
- DAT PIN, CLK PIN: Select each pin of the measurement module (GPIO4 ∼ GPIO27).
- Reference Unit: Enter the value obtained in Section 2.
- Number of measurements: Enter how many measurement results will be used to calculate the average value.

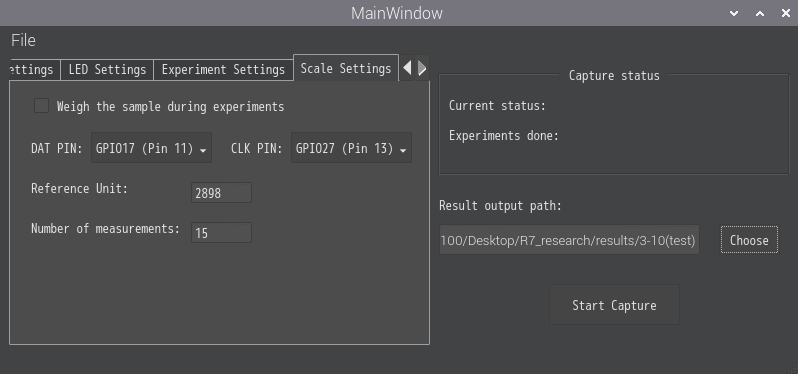
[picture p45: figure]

Figure 6: Scale Settings Tab

7

## 4 Experimental Procedure

1. Darken the test room (close the blinds, reduce the monitor brightness, etc.).
2. Place the sample on the scale and attach the plastic film cover.
3. Set the light source at an appropriate angle and fix it in place.
4. Cover the entire device with cardboard and orient the monitor in the opposite direction from the device.
5. Configure the various settings in capture.py.
6. Press the “Start Capture” button.

## 5 After the Experiment

1. Exit capture.py.
2. Remove the plant-based meat sample from the device and measure its mass again using hx711 scale.py (obtain the final mass mf ).
3. Turn off the DC power supplies used.
4. Save the data to a USB flash drive or any other memory device.
5. Turn off the Raspberry Pi(if data analysis is done on a regular computer).

8

## 6 Image Processing Procedure Using image.py

1. Use Geany to launch image.py (refer to Programs/Image Analysis Software)
2. Click “Open File” and select one image from the initial time when the near-infrared light source is turned on.

### 6.1 Blur and Thresholding

1. Select “Gaussian blur” from “Blur Method” and select “Thresh Binary” from “Thresholding Method”.
2. Set “Kernel” to (3, 3) and set “signalX” to 0.
3. Adjust the “Threshold Value” until the shape of the plant-based meat sample is clearly displayed, and take note of the value. Each time the settings are changed, click “Apply Settings” to update the image displayed on the right.

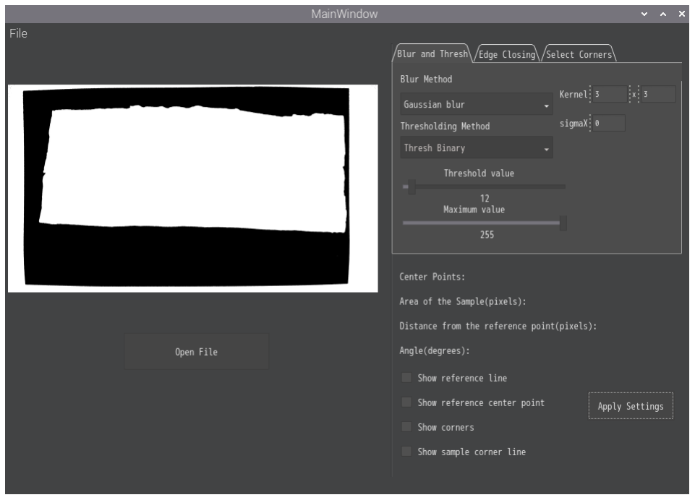
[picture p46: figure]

Figure 7: Blur and Thresh Tab

9

### 6.2 Edge Closing

1. Select “Edge Closing” and set “Kernel” to (3, 3).
2. Click the checkbox for “Area and Center Point Detection”.
3. Adjust “min area” and “max area” until the contour of the sample region is displayed with a yellow line, and take note of the values.
4. Enter the recorded values into another program and perform multiple image processing (calculation of APV and API for all images) (for details, see https://github.com/kostasb100/low-cost-plant-based-meat-moisture-device).

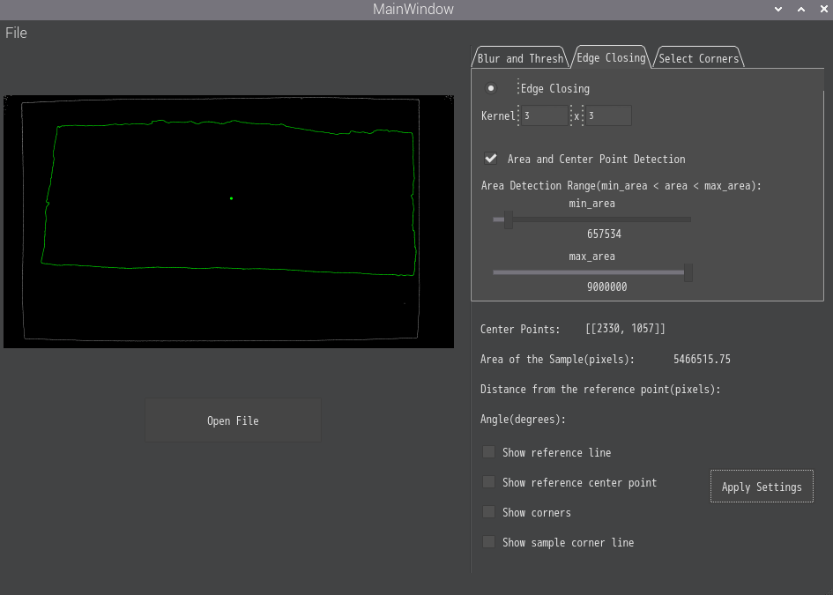
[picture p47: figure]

Figure 8: Edge Closing Tab

10

## 7 Troubleshooting

During the use of this device, there may be cases where the light sources (LEDs, near-infrared light source) do not turn on. In such cases, check the following steps.

### 7.1 Hardware

1. Using a multimeter check whether the power for every circuit(scale, infrared light source) is being delivered at the correct value. For LED circuits, check whether the pins are connected correctly.
2. Turn off the device and check the wiring (especially the wiring inside the device).
3. Try activating the near-infrared light source (LED circuits) using an external signal (a voltage source other than the Raspberry Pi GPIO pins).
4. For further details, refer to https://github.com/kostasb100/low-cost-plant-based-meatmoisture-device.

### 7.2 Software

This software may stop just before capturing raw images. In such cases, check the following steps.

1. Execute sudo apt update && sudo apt upgrade in the terminal.
2. Restart the Raspberry Pi.
3. For further details, refer to https://github.com/kostasb100/low-cost-plant-based-meatmoisture-device.

11

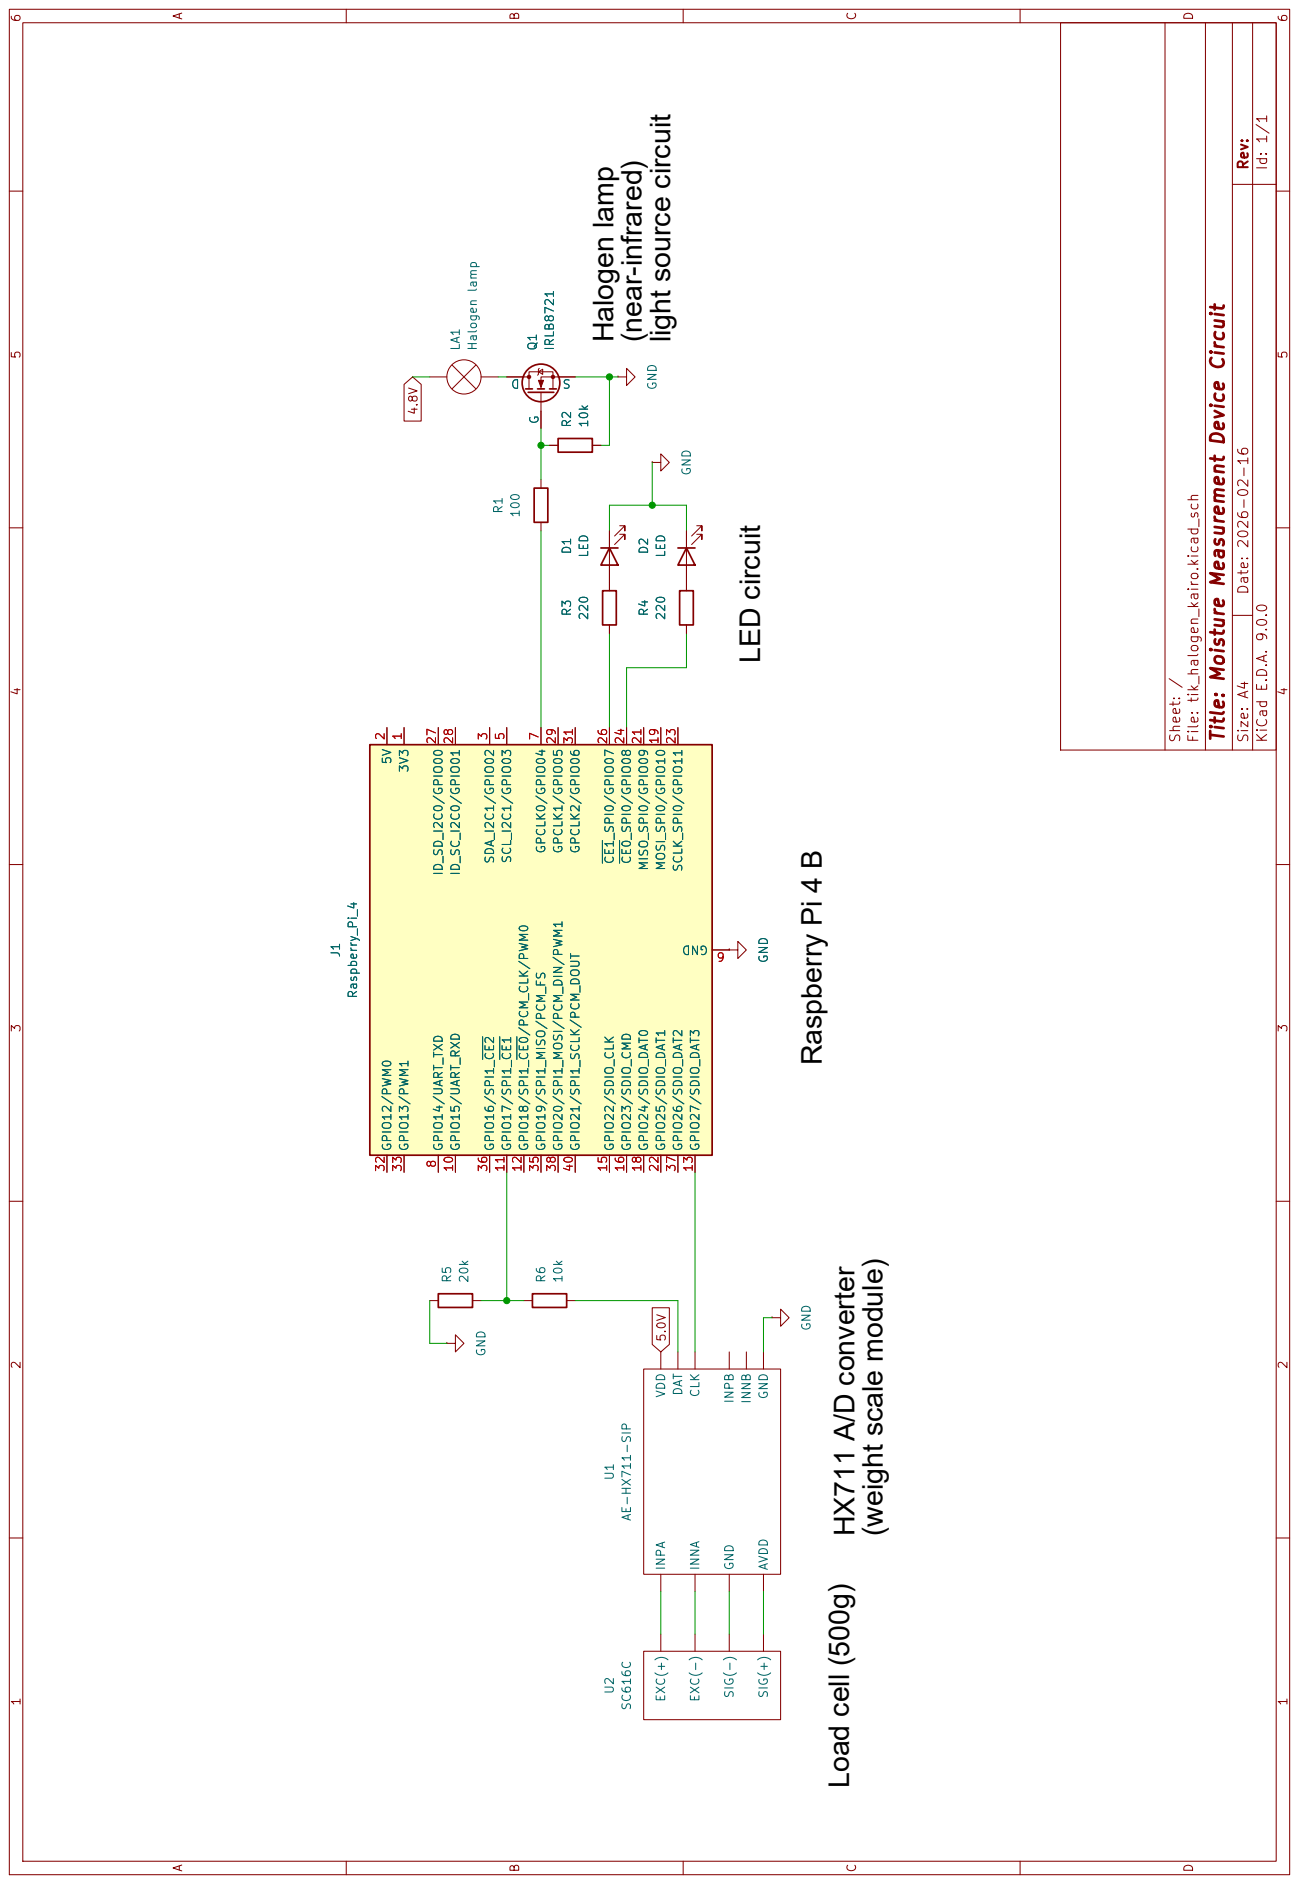
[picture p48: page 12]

D Date: 2026-02-16 KiCad E.D.A. 9.0.0 Rev: Size: A4

Id: 1/1 Title: Moisture Measurement Device Circuit File: tik_halogen_kairo.kicad_sch Sheet: /

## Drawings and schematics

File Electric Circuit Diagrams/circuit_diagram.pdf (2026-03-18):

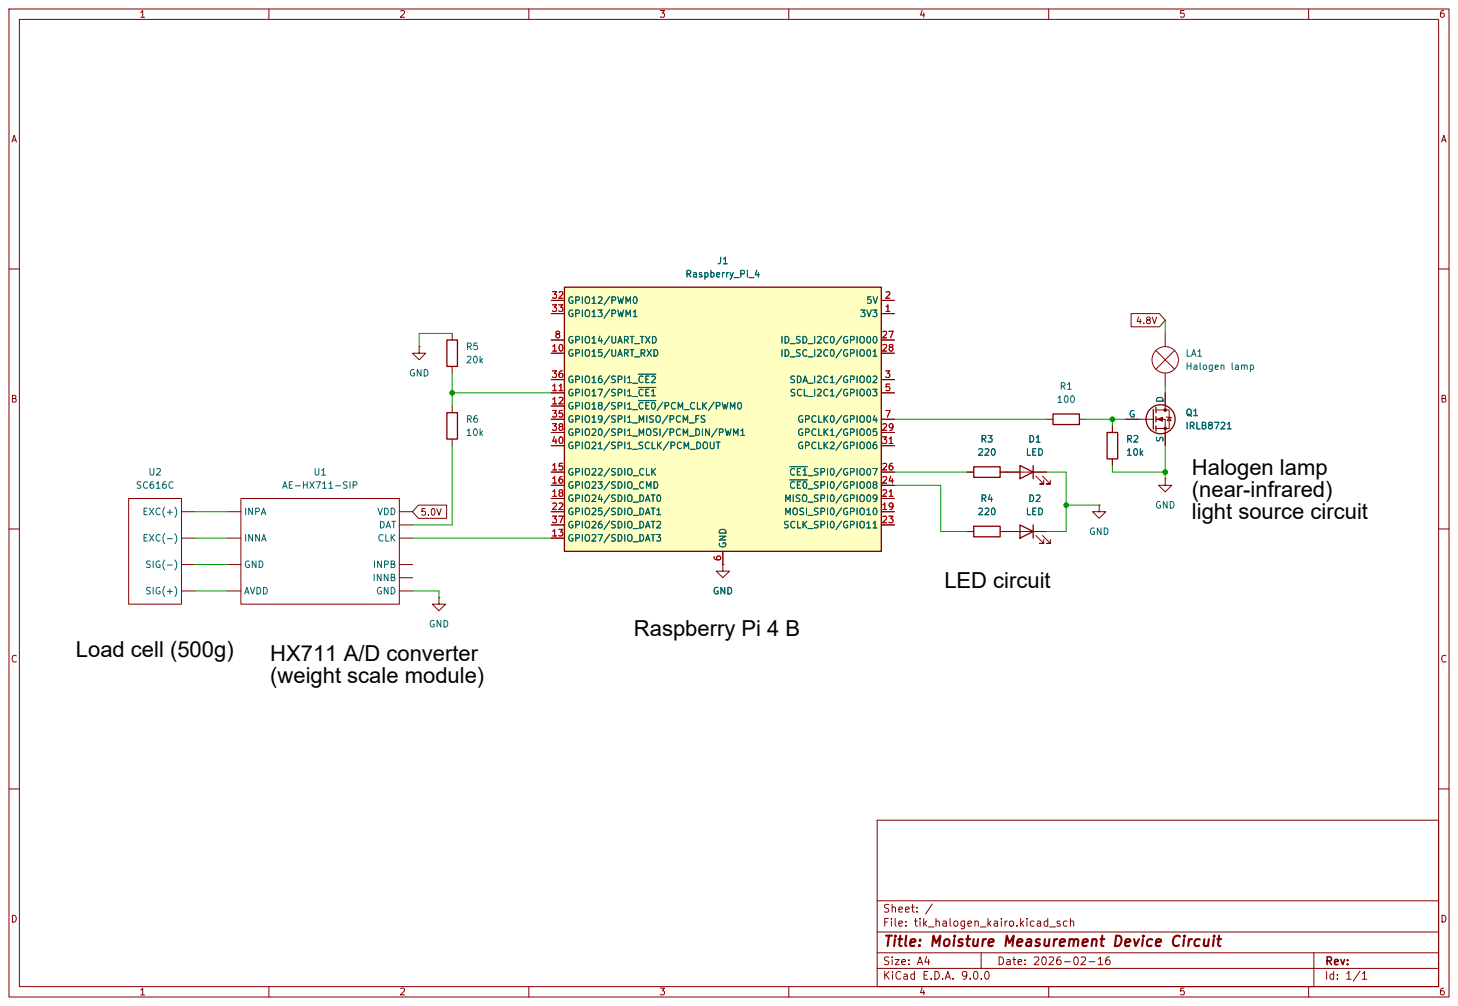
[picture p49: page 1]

Id: 1/1 Title: Moisture Measurement Device Circuit File: tik_halogen_kairo.kicad_sch Sheet: /

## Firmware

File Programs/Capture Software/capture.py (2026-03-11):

'''
Capture software 

This program:
- Captures noise(dark), halogen lamp illuminated and LED illuminated images
- Captures images in both JPEG and RAW(DNG) formats
- Let's the user set the Raspberry Pi Camera module settings manually
- Saves metadata of each capture
- Measures the weight of the sample using the HX711 AD-converter module
- Must be in the same folder as capture.ui

Purpose:
- Enables the user to do moisture analysis experiments using
  plant based meat samples and cells with water automatically
- Provides a GUI with which people with limited knowledge of 
  programming can still conduct such experiments with the
  Raspberry Pi 4 B microcontrollers.

2026-03
'''

from PyQt5.QtWidgets import (
    QMainWindow, QApplication, QPushButton, QLabel, QFileDialog,
    QRadioButton, QSlider, QComboBox, QLineEdit, QCheckBox, QAction,
    QMessageBox)
from picamera2 import Picamera2, Preview, controls
from PyQt5 import uic
from PyQt5.QtCore import QThread, pyqtSignal
from PyQt5.QtGui import QPixmap, QImage
import json, sys, os, time
import cv2 as cv
import numpy as np
import RPi.GPIO as GPIO
from hx711 import HX711


# DEFAULT camera and capture settings dictionary
DEFAULTS = {
    # Camera Settings
    "shutter_speed": "",
    "lens_position": "",
    "colour_gain_red": "",
    "colour_gain_blue": "",
    "analog_gain": "",
    "preheat": "",
    # Illuminated Capture Settings
    "illum_capture_check": False,
    "image_capture": "",
    "illum_raw": False,
    "pause_between_capture": "",
    "illuminated_image_name": "",
    "lamp_drive": "External source",
    # Noise Settings
    "noise_capture_check": False,
    "noise_raw": False,
    "noise_image_capture": "",
    "noise_image_name": "",
    "pause_between_noise_capture": "",
    # LED Settings
    "led_capture_check": False,
    "led1_combobox": "None",
    "led2_combobox": "None",
    "led_raw": False,
    "led_image_count": "None",
    "pause_between_led_capture": "None",
    "led_image_name": "",
    # Advanced Settings
    "metadata": False,
    "single_shutter": False,
    "multiple_shutter": False,
    "shutter_speed_from": "",
    "shutter_speed_to": "",
    "shutter_speed_by": "",
    "number_experiments": "",
    "time_between_experiments": "",
    # Scale Settings
    "scale_check": False,
    "dat": "None",
    "clk": "None",
    "ref_unit": "",
    "scale_num": "",
}

# Enable capture for each individual stage
# with user set settings
class SingleCaptureThread(QThread):

    def __init__(self, save_dir, main_title, image_count, pause_time,
                 picam2=None, save_metadata=False,save_raw=False, requested_controls=None):

        super().__init__()
        self.save_dir = save_dir
        self.main_title = main_title
        self.image_count = image_count
        self.pause_time = pause_time
        self.picam2 = picam2
        self.save_metadata = save_metadata
        self.save_raw = save_raw
        self.running = True
        self.requested_controls = requested_controls or {}

    def run(self):
        for i in range(self.image_count):
            if not self.running:
                break

            filename = f"{self.main_title}{i}.jpg"
            filepath = os.path.join(self.save_dir, filename)

            if self.picam2:
                request = self.picam2.capture_request()

                # Save JPEG images
                request.save("main", filepath)

                # Save RAW(DNG) images
                if self.save_raw:
                    raw_path = os.path.splitext(filepath)[0] + ".dng"
                    request.save_dng(raw_path)

                # Save metadata of individual images
                metadata = request.get_metadata()

                request.release()

                # Image Metadata Storage
                if self.save_metadata:
                    metadata = self.picam2.capture_metadata()

                    # JSON file name matches image name
                    json_path = os.path.join(
                        self.save_dir,
                        f"{self.main_title}{i}.json"
                    )

                    # Ensure everything is JSON-serializable
                    def convert(obj):
                        if isinstance(obj, (tuple, list)):
                            return list(obj)
                        if hasattr(obj, "tolist"):
                            return obj.tolist()
                        return obj

                    clean_metadata = {k: convert(v) for k, v in metadata.items()}
                    clean_requested = {k: convert(v) for k, v in self.requested_controls.items()}

                    json_path = os.path.splitext(filepath)[0] + ".json"

                    with open(json_path, "w") as f:
                        json.dump(
                            {
                                "requested": clean_requested,
                                "metadata": clean_metadata
                            },
                            f,
                            indent=4
                        )

            print(f"{filename}: {filepath}")
            
            time.sleep(self.pause_time)

class UI(QMainWindow):
    def __init__(self):
        super(UI, self).__init__()
        uic.loadUi("capture.ui", self)
        self.show()
        
        # Set widgets of the GUI
        self.capture_button = self.findChild(QPushButton, "pushButton")
        self.choose_experiment_output_path_button = self.findChild(QPushButton, "pushButton_2")

        self.shutter_speed = self.findChild(QLineEdit, "lineEdit")
        self.lens_position = self.findChild(QLineEdit, "lineEdit_2")
        self.colour_gains_red = self.findChild(QLineEdit, "lineEdit_3")
        self.analog_gain = self.findChild(QLineEdit, "lineEdit_5")
        self.colour_gains_blue = self.findChild(QLineEdit, "lineEdit_6")

        self.illuminated_capture_checkbox = self.findChild(QCheckBox, "checkBox_8")
        self.illuminated_image_count = self.findChild(QLineEdit, "lineEdit_8")
        self.pause_between_illuminated_capture = self.findChild(QLineEdit, "lineEdit_9")
        self.save_illum_raw_checkbox = self.findChild(QCheckBox, "checkBox_4")
        self.illuminated_image_name = self.findChild(QLineEdit, "lineEdit_14")
        self.lamp_drive_combobox = self.findChild(QComboBox, "comboBox")

        self.noise_capture_checkbox = self.findChild(QCheckBox, "checkBox_9")
        self.noise_image_count = self.findChild(QLineEdit, "lineEdit_10")
        self.pause_between_noise_capture = self.findChild(QLineEdit, "lineEdit_11")
        self.save_noise_raw_checkbox = self.findChild(QCheckBox, "checkBox_6")
        self.noise_image_name = self.findChild(QLineEdit, "lineEdit_13")

        self.led_capture_checkbox = self.findChild(QCheckBox, "checkBox_5")
        self.led1_combobox = self.findChild(QComboBox, "comboBox_3")
        self.led2_combobox = self.findChild(QComboBox, "comboBox_6")
        self.led_image_count = self.findChild(QLineEdit, "lineEdit_27")
        self.pause_between_led_capture = self.findChild(QLineEdit, "lineEdit_26")
        self.save_led_raw_checkbox = self.findChild(QCheckBox, "checkBox_7")
        self.led_image_name = self.findChild(QLineEdit, "lineEdit_24")

        self.single_shutter_speed_radiobutton = self.findChild(QRadioButton, "radioButton")
        self.mult_shutter_speeds_radiobutton = self.findChild(QRadioButton, "radioButton_2")
        self.shutter_time_from = self.findChild(QLineEdit, "lineEdit_15")
        self.shutter_time_to = self.findChild(QLineEdit, "lineEdit_16")
        self.shutter_time_by = self.findChild(QLineEdit, "lineEdit_17")
        self.pre_heat_time = self.findChild(QLineEdit, "lineEdit_18")
        self.experiment_output_path = self.findChild(QLineEdit, "lineEdit_19")
        self.time_between_experiments = self.findChild(QLineEdit, "lineEdit_20")

        self.current_status = self.findChild(QLabel, "label_32")
        self.number_of_experiments = self.findChild(QLineEdit, "lineEdit_21")

        self.scale_measurement_checkbox = self.findChild(QCheckBox, "checkBox_3")
        self.dat_combobox = self.findChild(QComboBox, "comboBox_2")
        self.clk_combobox = self.findChild(QComboBox, "comboBox_4")
        self.ref_unit_lineedit = self.findChild(QLineEdit, "lineEdit_22")
        self.scale_measurement_number_lineedit = self.findChild(QLineEdit, "lineEdit_23")
        self.experiments_done_label = self.findChild(QLabel, "label_33")

        self.actionNew = self.findChild(QAction, "actionNew")
        self.actionLoad = self.findChild(QAction, "actionLoad")
        self.actionSave = self.findChild(QAction, "actionSave")
        self.actionSave_as = self.findChild(QAction, "actionSave_As")

        self.actionNew.triggered.connect(self.new_settings)
        self.actionLoad.triggered.connect(self.load_settings)
        self.actionSave.triggered.connect(self.save_settings)
        self.actionSave_as.triggered.connect(self.save_settings_as)

        self.get_metada_checkbox = self.findChild(QCheckBox, "checkBox_2")
        self.choose_experiment_output_path_button.clicked.connect(self.choose_directory_capture)

        self.capture_button.clicked.connect(self.start_capture)

        self.camera_available = True
        self.picam2 = Picamera2()

        # Set a dictionary for describing different stage of the experiments
        self.capture_status = {
            "scale": "Scaling the sample...",
            "init_camera": "Initializing camera...",
            "led_capture": "Capturing LED images",
            "noise_capture": "Capturing noise images...",
            "preheat_lamp": "Preheating the lamp...",
            "image_capture": "Capturing illuminated images...",
            "idle": "Idle...",
            "complete": "Experiment completed",
        }

                # GPIO pin mapping for easy reference
        self.gpio_mapping = {
            "GPIO2 (Pin 3)": 2,
            "GPIO3 (Pin 5)": 3,
            "GPIO4 (Pin 7)": 4,
            "GPIO5 (Pin 29)": 5,
            "GPIO6 (Pin 31)": 6,
            "GPIO7 (Pin 26)": 7,
            "GPIO8 (Pin 24)": 8,
            "GPIO9 (Pin 21)": 9,
            "GPIO10 (Pin 19)": 10,
            "GPIO11 (Pin 23)": 11,
            "GPIO12 (Pin 32)": 12,
            "GPIO13 (Pin 33)": 13,
            "GPIO14 (Pin 8)": 14,
            "GPIO15 (Pin 10)": 15,
            "GPIO16 (Pin 36)": 16,
            "GPIO17 (Pin 11)": 17,
            "GPIO18 (Pin 12)": 18,
            "GPIO19 (Pin 35)": 19,
            "GPIO20 (Pin 38)": 20,
            "GPIO21 (Pin 40)": 21,
            "GPIO22 (Pin 15)": 22,
            "GPIO23 (Pin 16)": 23,
            "GPIO24 (Pin 18)": 24,
            "GPIO25 (Pin 22)": 25,
            "GPIO26 (Pin 37)": 26,
            "GPIO27 (Pin 13)": 27
        }
        
        GPIO.setmode(GPIO.BCM)

    def set_capture_status(self, status_key):
        if status_key in self.capture_status:
            self.current_status.setText(self.capture_status[status_key])
        QApplication.processEvents()
    
    # Enable LED control
    def set_led_high(self, pin):
        if pin is not None:
            GPIO.output(pin, GPIO.HIGH)

    def set_led_low(self, pin):
        if pin is not None:
            GPIO.output(pin, GPIO.LOW)
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
